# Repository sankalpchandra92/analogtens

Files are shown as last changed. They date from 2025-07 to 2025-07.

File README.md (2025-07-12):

# Analog TENS Circuit
This project is based on a TENS (Transcutaneous Electrical Nerve Stimulation) unit, which is used to temporarily treat chronic or acute pain by delivering low-voltage electrical currents to the affected area through the skin.
## Waveform Generation
- An astable 555 timer circuit was first designed to generate a pulse train with the desired frequency.
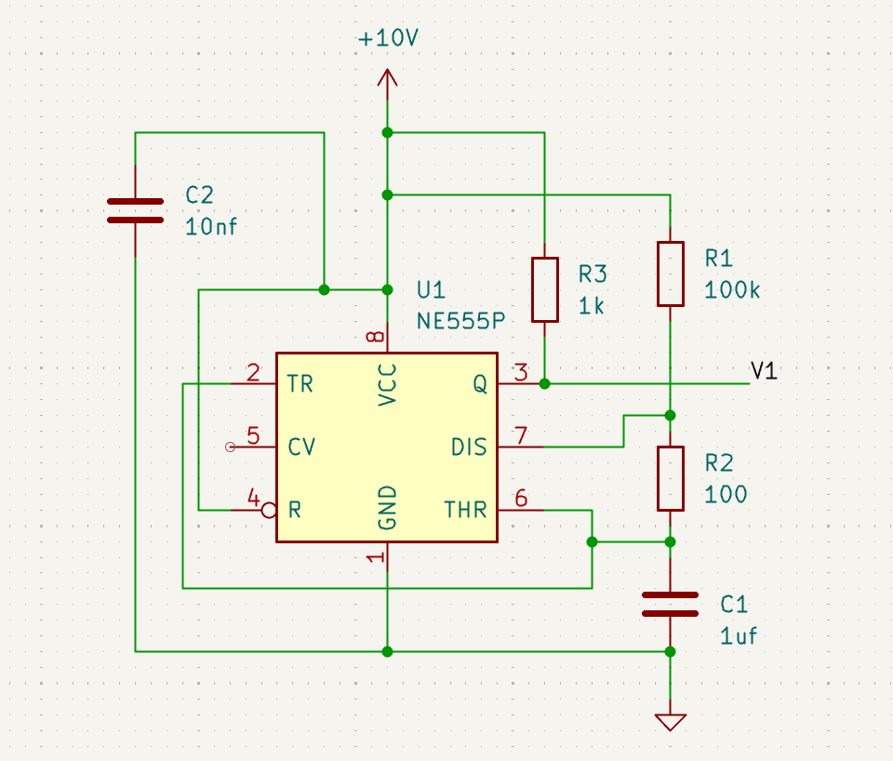
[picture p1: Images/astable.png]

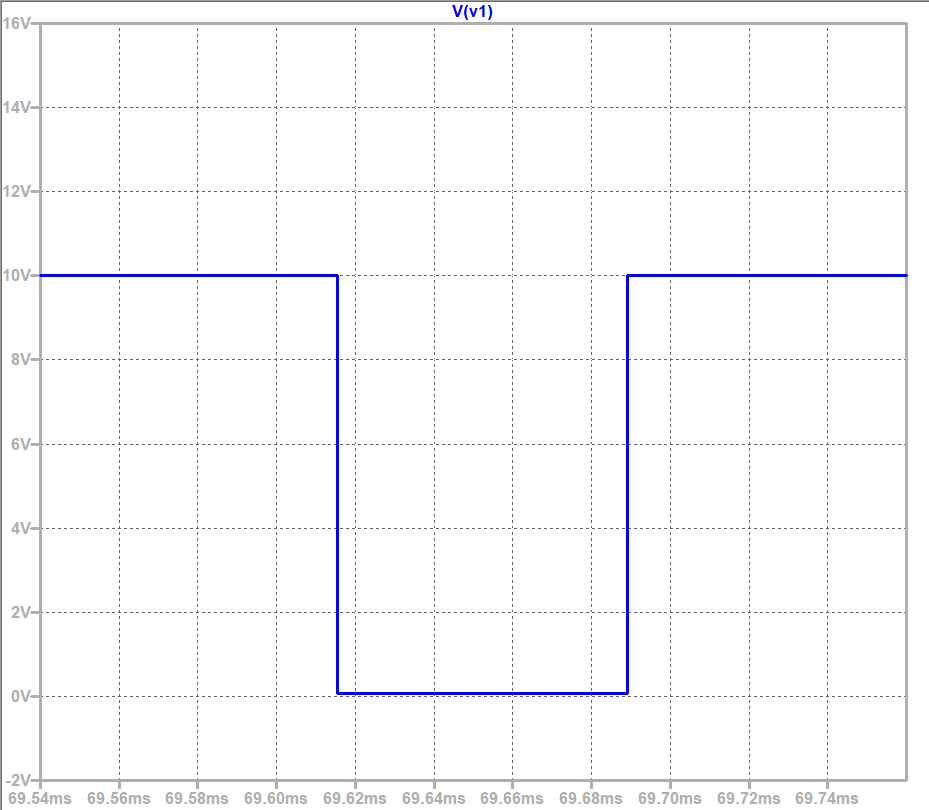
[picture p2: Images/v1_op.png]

- The timing resistors were adjusted for the desired frequency.
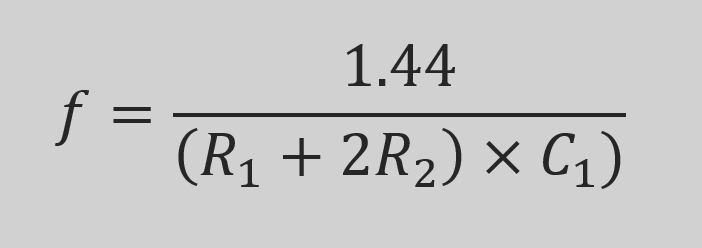
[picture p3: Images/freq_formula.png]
Formula

- This signal was used to trigger a monostable 555 timer, configured to produce a pulse of the desired width on each falling edge.
- A differentiator circuit was then used to extract the falling edge of the monostable output, which was used to trigger a second monostable timer, producing an equal-width pulse.
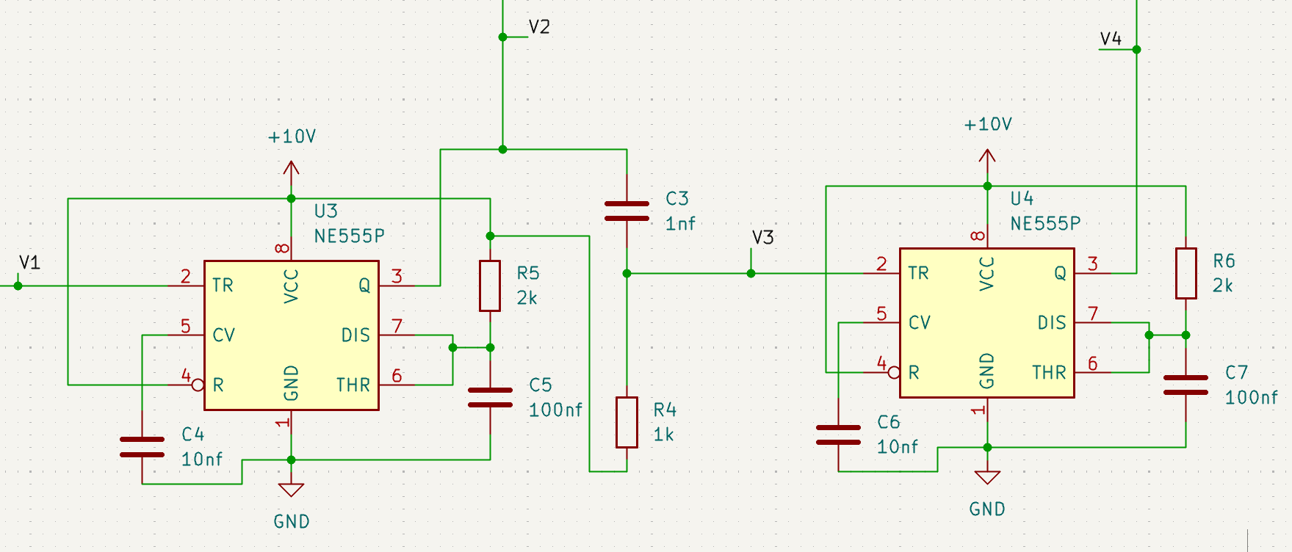
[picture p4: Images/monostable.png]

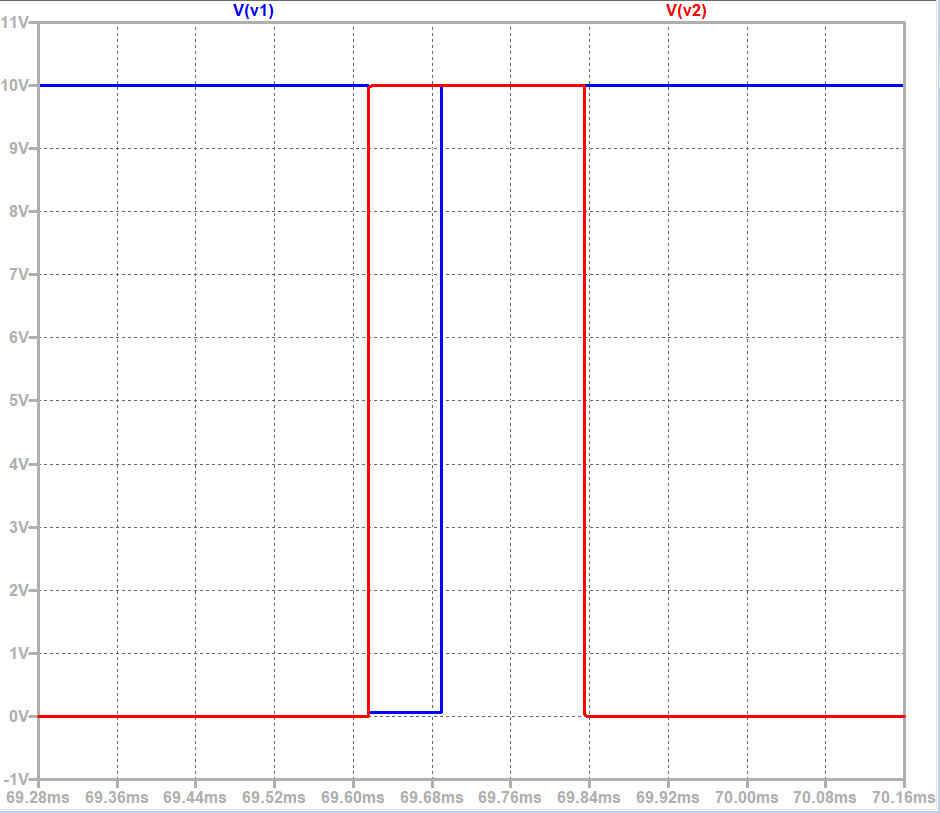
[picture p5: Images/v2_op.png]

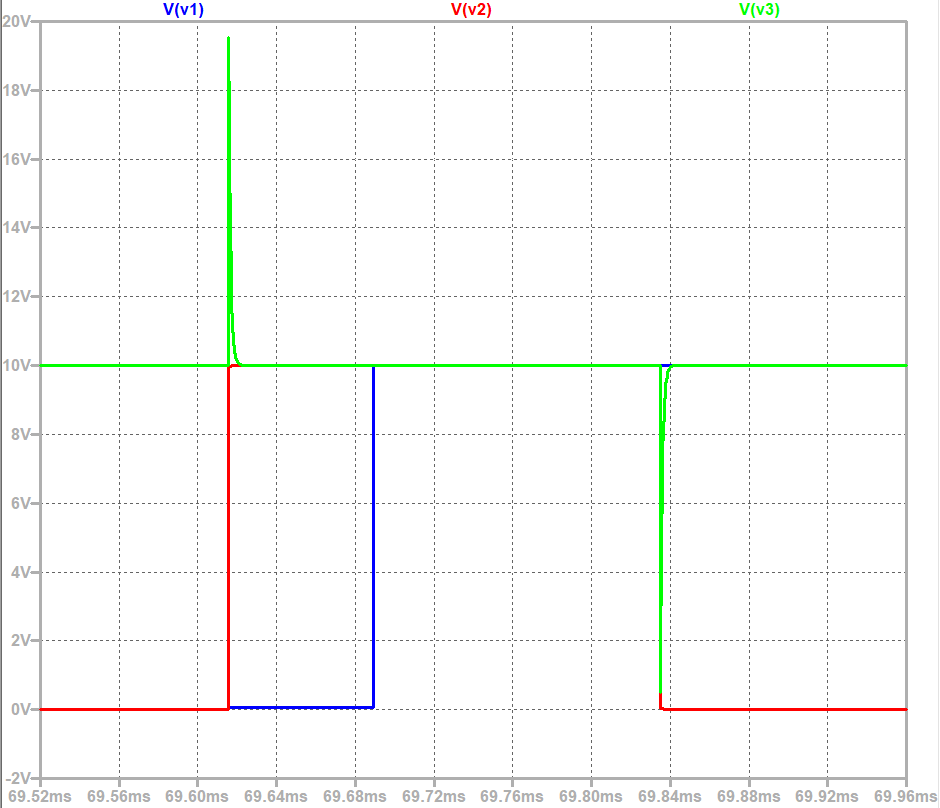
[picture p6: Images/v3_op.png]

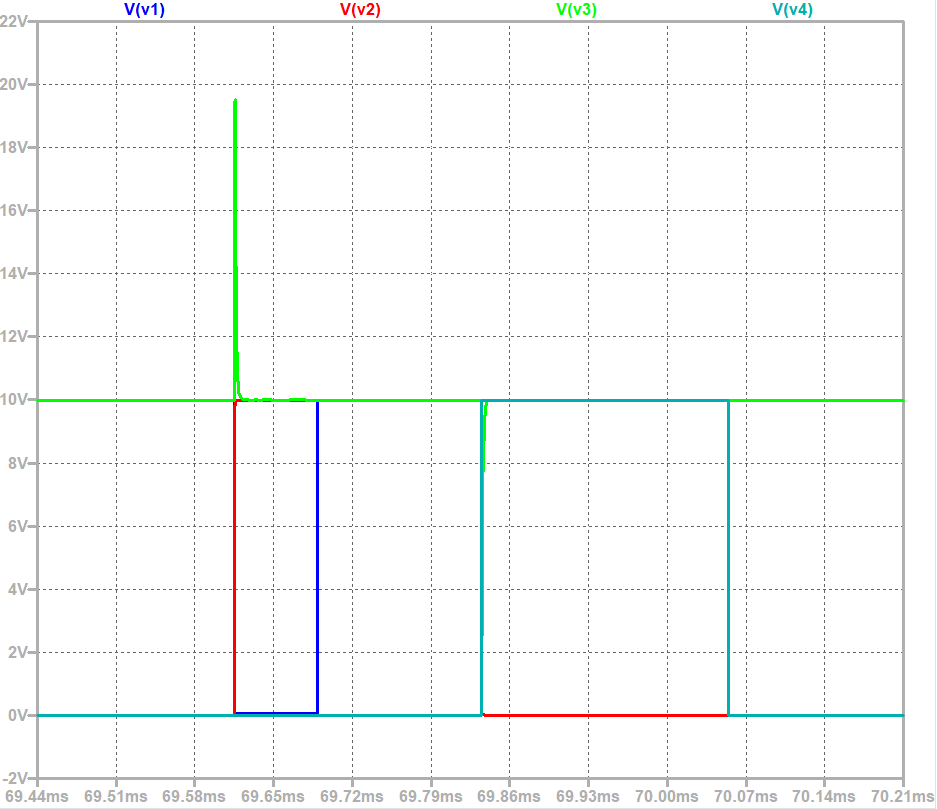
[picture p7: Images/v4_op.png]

- The timing resistors of the monostable stage circuit were adjusted for the desired pulse width.
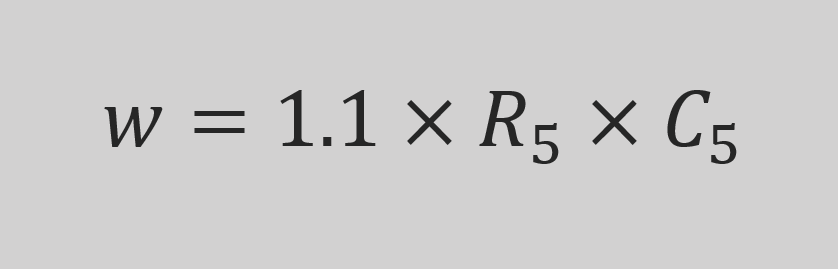
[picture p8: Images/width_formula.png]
Formula

- Final waveform was produced with a pulse width of about 200 &micro;s at a frequency of 14 Hz.
## Signal Conditioning
- The output signal from the first monostable timer is fed into a non-inverting operational amplifier to buffer and isolate the waveform.
- The signal from the second monostable timer is passed through an inverting operational amplifier to produce a polarity-reversed pulse.
- Both amplifier outputs are routed through current-limiting resistors to ensure safe delivery of the stimulation pulses.
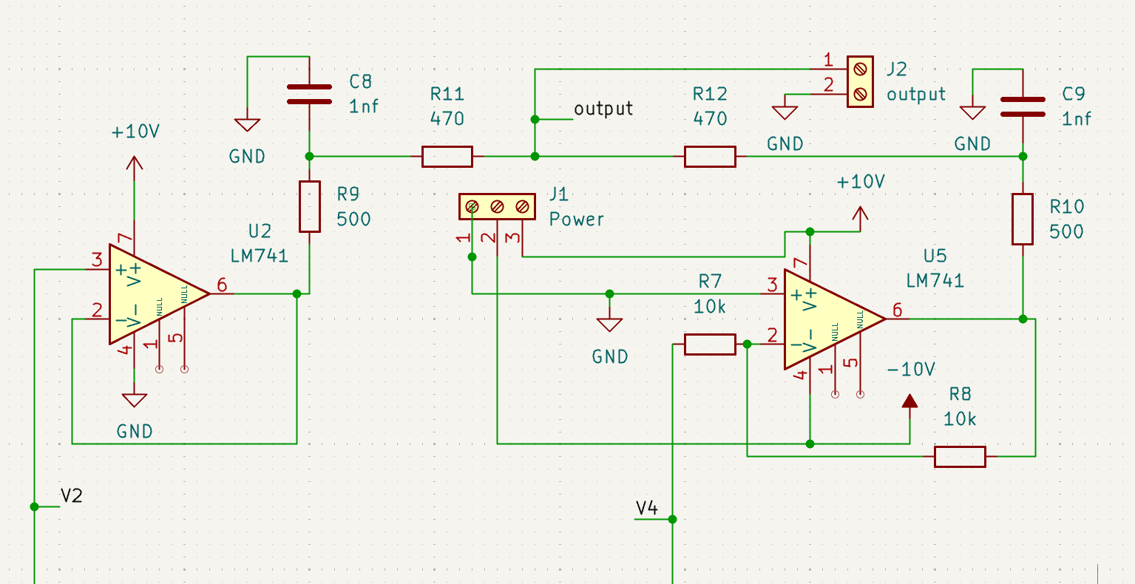
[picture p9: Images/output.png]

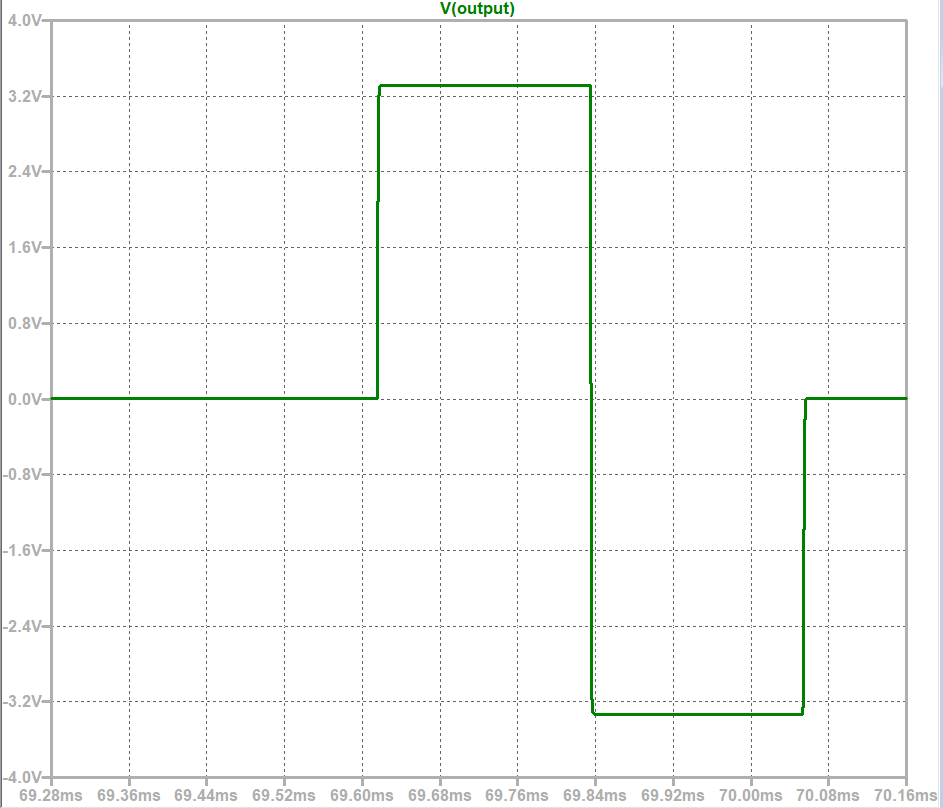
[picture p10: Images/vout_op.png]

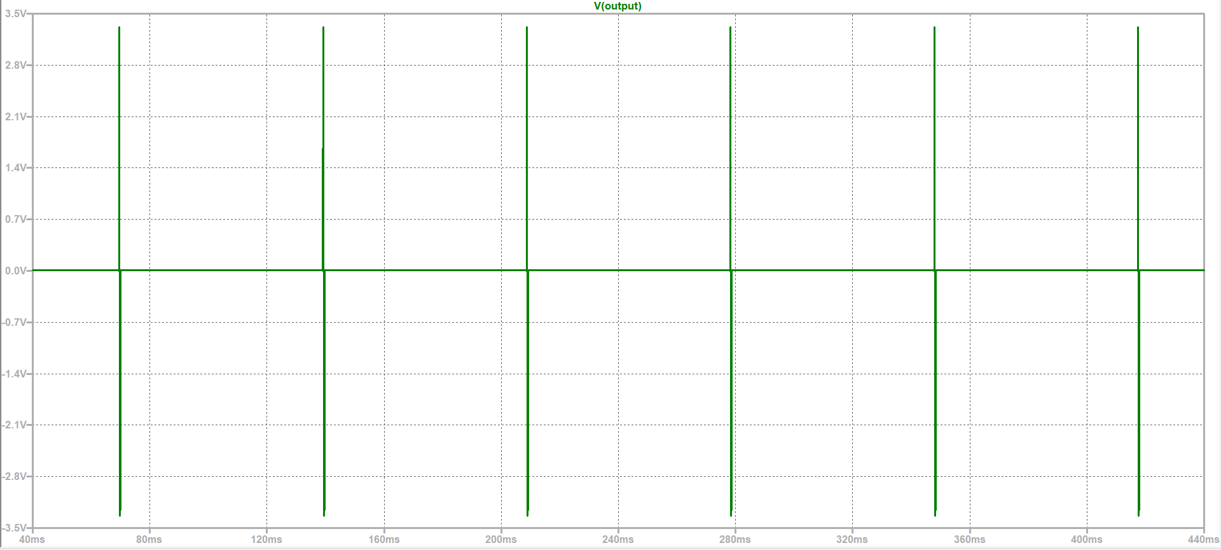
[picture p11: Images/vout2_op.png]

- The circuit was simulated in LTspice with various output loads between 1 k&Omega; and 10 k&Omega; (representing typical skin resistance), verifying that the maximum output current remained below 3.5 mA.
## PCB Layout
The schematic was converted into a dual-layer PCB layout, designed for reliable hardware testing and future prototyping. 
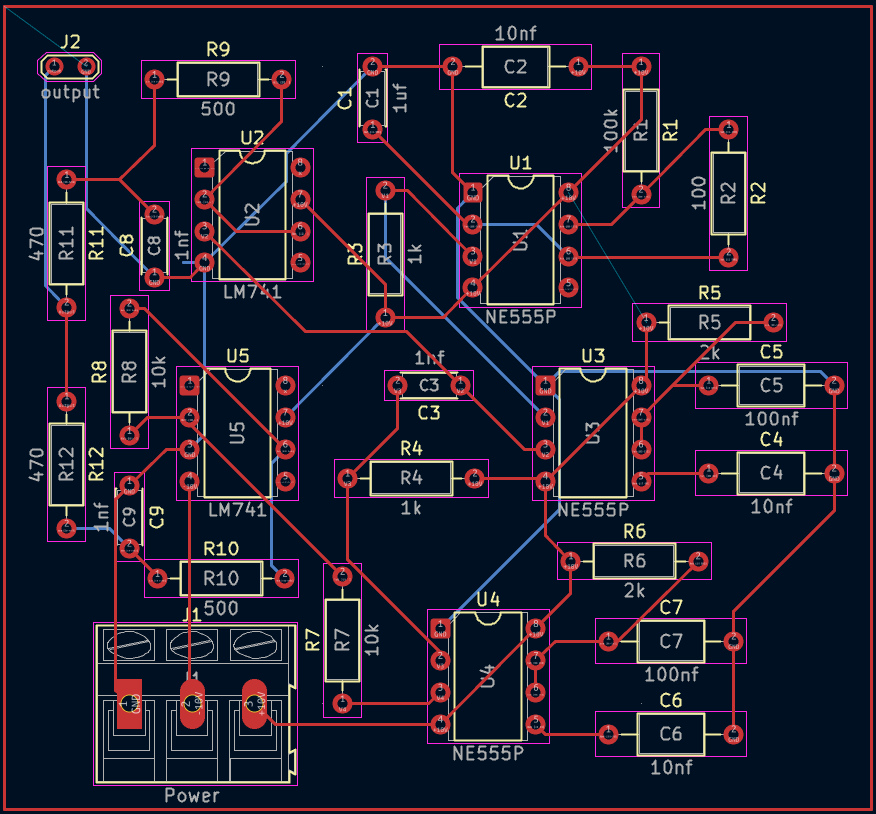
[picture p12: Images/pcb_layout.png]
PCB_Layout


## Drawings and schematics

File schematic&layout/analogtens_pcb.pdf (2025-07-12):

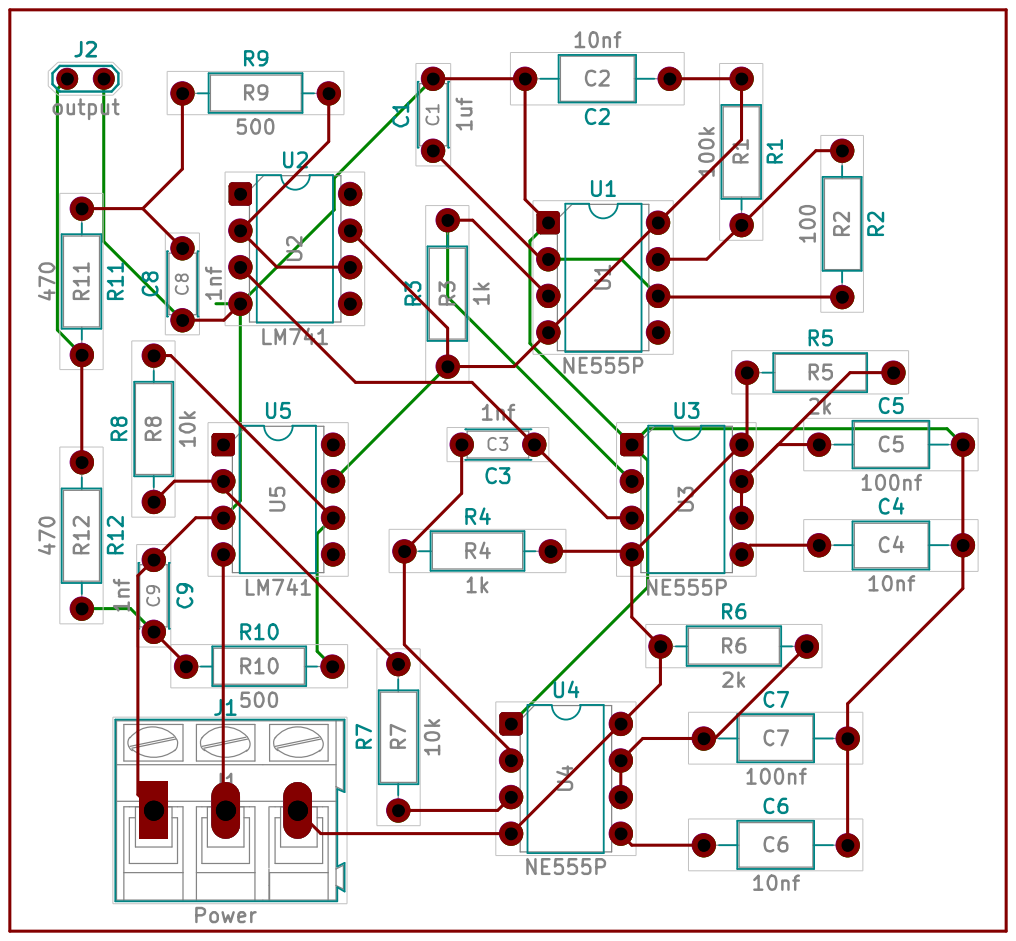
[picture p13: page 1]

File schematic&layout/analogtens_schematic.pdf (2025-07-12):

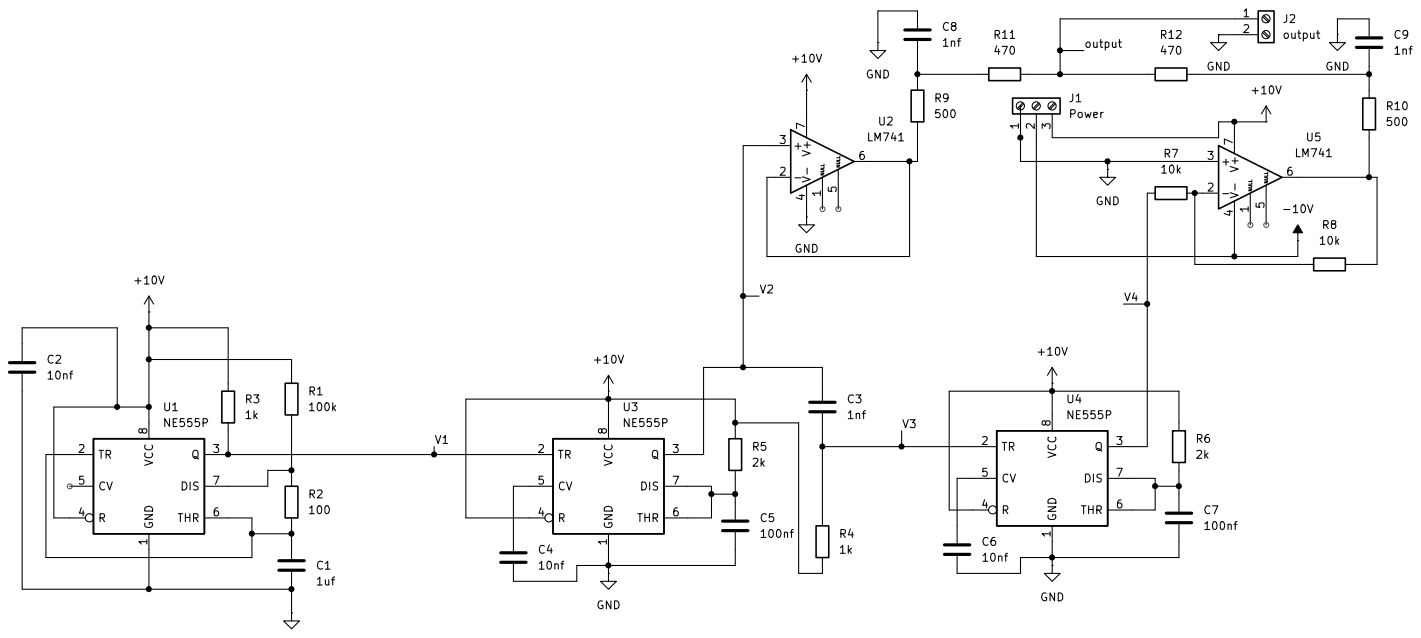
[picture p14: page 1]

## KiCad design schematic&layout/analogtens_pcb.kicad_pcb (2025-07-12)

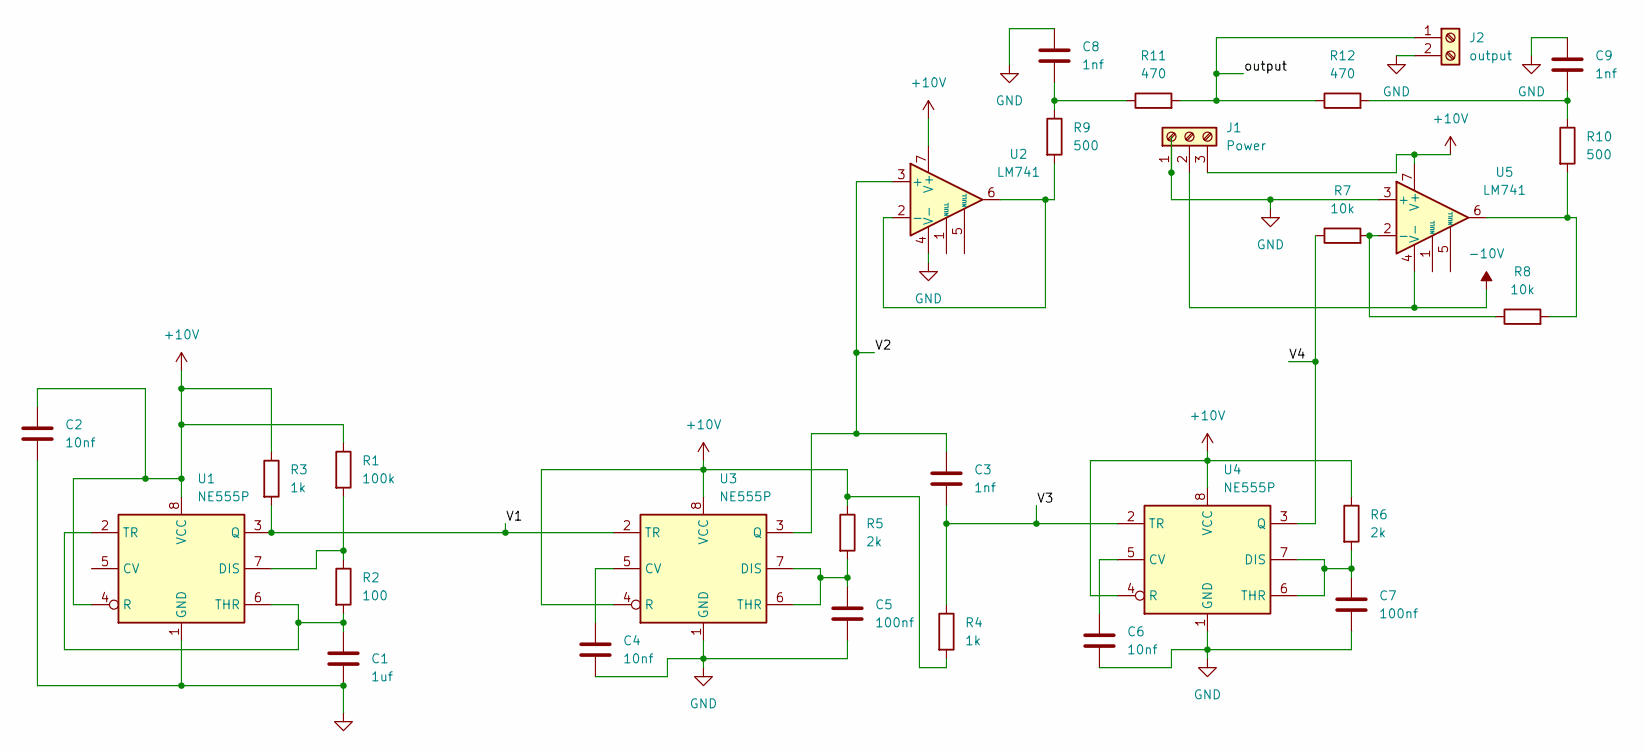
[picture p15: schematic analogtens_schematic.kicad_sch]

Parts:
C1: 1uf; C_Disc_D4.3mm_W1.9mm_P5.00mm
C2, C4, C6: 10nf; C_Axial_L5.1mm_D3.1mm_P10.00mm_Horizontal
C3, C8, C9: 1nf; C_Disc_D4.3mm_W1.9mm_P5.00mm
C5, C7: 100nf; C_Axial_L5.1mm_D3.1mm_P10.00mm_Horizontal
J1: Power; TerminalBlock_Altech_AK300-3_P5.00mm
J2: output; TestPoint_2Pads_Pitch2.54mm_Drill0.8mm
R1: 100k; R_Axial_DIN0207_L6.3mm_D2.5mm_P10.16mm_Horizontal
R2: 100; R_Axial_DIN0207_L6.3mm_D2.5mm_P10.16mm_Horizontal
R3, R4: 1k; R_Axial_DIN0207_L6.3mm_D2.5mm_P10.16mm_Horizontal
R5, R6: 2k; R_Axial_DIN0207_L6.3mm_D2.5mm_P10.16mm_Horizontal
R7, R8: 10k; R_Axial_DIN0207_L6.3mm_D2.5mm_P10.16mm_Horizontal
R9, R10: 500; R_Axial_DIN0207_L6.3mm_D2.5mm_P10.16mm_Horizontal
R11, R12: 470; R_Axial_DIN0207_L6.3mm_D2.5mm_P10.16mm_Horizontal
U1, U3, U4: NE555P; DIP-8_W7.62mm
U2, U5: LM741; DIP-8_W7.62mm

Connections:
+10V: C2.1, J1.3, R1.1, R3.1, R4.2, R5.1, R6.1, U1.4 (R), U1.8 (VCC), U2.7 (V+), U3.4 (R), U3.8 (VCC), U4.4 (R), U4.8 (VCC), U5.7 (V+)
-10V: J1.2, U5.4 (V-)
/V1: R3.2, U1.3 (Q), U3.2 (TR)
/V2: C3.1, U2.3 (+), U3.3 (Q)
/V3: C3.2, R4.1, U4.2 (TR)
/V4: R7.1, U4.3 (Q)
/output: J2.1, R11.2, R12.1
GND: C1.2, C2.2, C4.2, C5.2, C6.2, C7.2, C8.1, C9.1, J1.1, J2.2, U1.1 (GND), U2.4 (V-), U3.1 (GND), U4.1 (GND), U5.3 (+)
unnamed: C8.2, R9.1, R11.1
unnamed: C9.2, R10.1, R12.2
unnamed: R8.2, R10.2, U5.6
unnamed: R1.2, R2.1, U1.7 (DIS)
unnamed: C1.1, R2.2, U1.2 (TR), U1.6 (THR)
unnamed: R9.2, U2.2 (-), U2.6
unnamed: C4.1, U3.5 (CV)
unnamed: C5.1, R5.2, U3.6 (THR), U3.7 (DIS)
unnamed: C6.1, U4.5 (CV)
unnamed: C7.1, R6.2, U4.6 (THR), U4.7 (DIS)
unnamed: R7.2, R8.1, U5.2 (-)

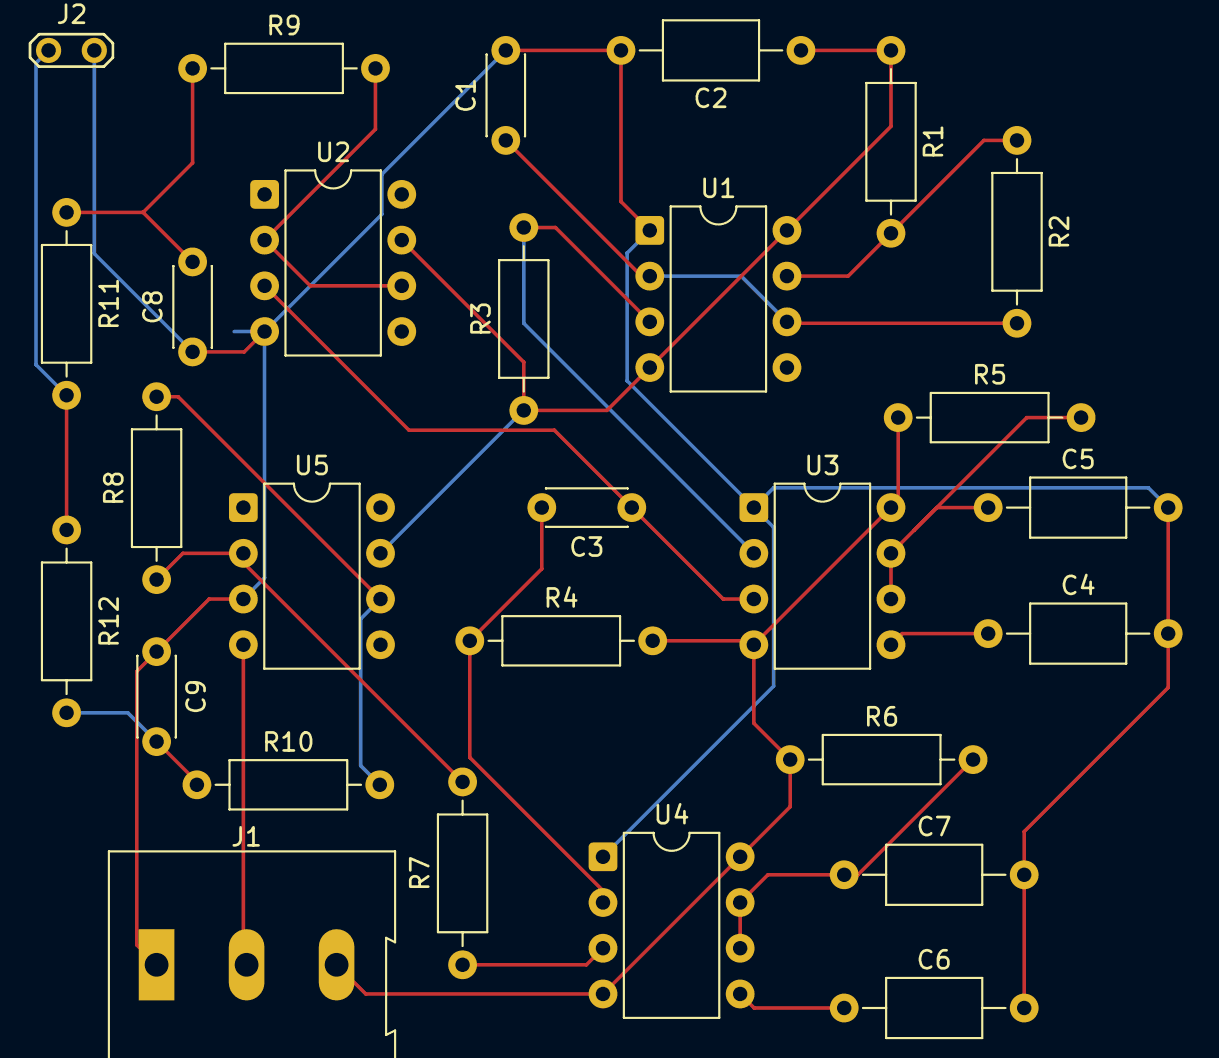
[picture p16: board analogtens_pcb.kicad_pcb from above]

Board: 2 copper layers, 28 parts (0 on the bottom side), 19 nets.
